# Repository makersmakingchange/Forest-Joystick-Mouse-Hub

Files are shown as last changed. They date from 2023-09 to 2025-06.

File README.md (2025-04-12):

# Forest Joystick Mouse Hub

## Overview
The Forest Hub enables a user to connect an analog joystick and up to four assistive switches to emulate a USB Mouse or USB Gamepad. As a USB Mouse, the joystick controls cursor movement and the assistive switches activate the left mouse button, right mouse button, middle mouse button, and scroll. As a USB Mouse, the joystick maps to the joystick/thumbstick and the assistive switches map to the joystick buttons. An additional assistive switch can be attached to the Hub to cycle between three setting slots and change the output mode between USB Mouse mode and USB Gamepad mode.

The device is comprised of a custom printed circuit board, off-the-shelf electronics, and 3D printed parts. The overall cost of materials for a single build is about $100. The individual unit cost cost is closer to $55. 

The Forest Hub is open assistive technology (OpenAT). Under the terms of the open source licenses, the device may be built, used, and improved upon by anyone.

Last updated: 2024-Apr-17
The latest version (V2.1) includes a new easier to use LED jig, updated firmware with center calibration, and updated documentation.
An updated version of the PCB and enclosure has been released (V2.0.1, 2024-Feb-20). The last version of the Forest Hub (v2.0.1) has been built and tested.

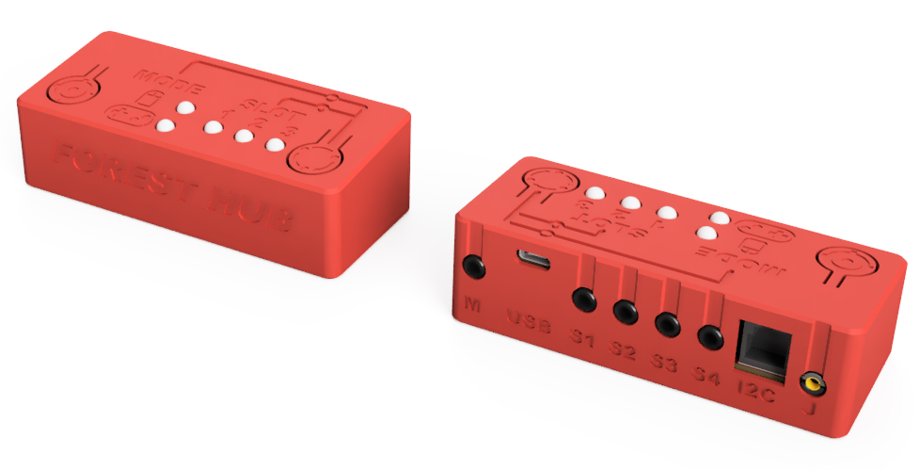
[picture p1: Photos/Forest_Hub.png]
A Forest Hub in a red enclosure.


MMC Assistive Device Library Listing: https://makersmakingchange.com/s/product/forest-joystick-mouse-hub/01tJR000000E4bdYAC

## OpenAT Joysticks
This design is part of the [OpenAT Joystick Project](https://github.com/makersmakingchange/OpenAT-Joysticks), a collection of open source designs for digital access and adapted gaming.  

## How to Obtain the Device
### 1. Do-it-Yourself (DIY) or Do-it-Together (DIT)

This is an open-source assistive technology, so anyone is free to build it. All of the files and instructions required to build the device are contained within this repository. Refer to the Maker Guide below.

### 2. Request a build of this device

If you would like to obtain a Forest Hub, you may submit a build request through the [MMC Assistive Device Library Listing](https://makersmakingchange.com/s/product/forest-joystick-mouse-hub/01tJR000000E4bdYAC) to have a volunteer maker build the device. As the requestor, you are responsible for reimbursing the maker for the cost of materials and any shipping.

### 3. Build this device for someone else

If you have the skills and equipment to build this device, and would like to donate your time to create the switch for someone who needs it, visit the [MMC Maker Wanted](https://makersmakingchange.com/maker-wanted/) section.

## Build Instructions

### 1. Read through the Maker Guide

The [Maker Guide](/Documentation/Forest_Hub_Maker_Guide.pdf) contains all the necessary information to build the device.

### 2. Use the Maker Checklist
Use the Maker Checklist in the [Maker Guide](/Documentation/Forest_Hub_Maker_Guide.pdf) to confirm details and customization options with the user.

### 3. Order the Custom Printed Circuit Board (PCB)
The manufacturing files for the PCB are located in the [PCB_Build_Files](/Build_Files/PCB_Build_Files/) folder.

### 4. Order the Off-The-Shelf Components

The [Bill of Materials](/Documentation/Forest_Hub_BOM.xlsx) lists all of the parts and 3D printed components required to build the device. 

### 5. Print the 3D Printable components

The print files can be found in the [/Build_Files/3D_Printing_Files](/Build_Files/3D_Printing/) folder.

### 6.  Assemble the Device

Reference the Assembly Guide section in the [Maker Guide](/Documentation/Forest_Hub_Maker_Guide.pdf) for the tools and steps required to build the device.

## Files
### Documentation
| Document             | Version | Link |
|----------------------|---------|------|
| Design Rationale     | 2.1     | [Forest_Hub_Design_Rationale](/Documentation/Forest_Hub_Design_Rationale.pdf)     |
| Maker Guide          | 2.1     | [Forest_Hub_Maker_Guide](/Documentation/Forest_Hub_Maker_Guide.pdf)     |
| Bill of Materials    | 2.1     | [Forest_Hub_Bill_of_Materials](/Documentation/Forest_Hub_BOM.csv)     |
| User Guide           | 2.1     | [Forest_Hub_User_Guide](/Documentation/Forest_Hub_User_Guide.pdf)    |
| Changelog            | 2.1     | [Changes](Changes.txt)     |

### Design Files
 - [CAD design Files](/Design_Files/CAD_Design_Files)
 - [PCB Design Files](/Design_Files/PCB_Design_Files)

### Build Files
 - [3D Printing Files](/Build_Files/3D_Printing_Files)
 - [PCB Build Files](/Build_Files/PCB_Build_Files/)
 - [Firmware Files](/Build_Files/Firmware_Files)

## License
Copyright (c) 2023 Neil Squire Society.

This repository describes Open Hardware:
 - Everything needed or used to design, make, test, or prepare the Forest Hub is licensed under the [CERN 2.0 Weakly Reciprocal license (CERN-OHL-W v2) or later](https://cern.ch/cern-ohl ) .
 - All software is under the [GNU General Public License v3.0 (GPL-3.0)](https://www.gnu.org/licenses/gpl.html).
 - Accompanying material such as instruction manuals, videos, and other copyrightable works that are useful but not necessary to design, make, test, or prepare the Forest Hub are published under a [Creative Commons Attribution-ShareAlike 4.0 license (CC BY-SA 4.0)](https://creativecommons.org/licenses/by-sa/4.0/) .

You may redistribute and modify this documentation and make products using it under the terms of the [CERN-OHL-W v2](https://cern.ch/cern-ohl).
This documentation is distributed WITHOUT ANY EXPRESS OR IMPLIED WARRANTY, INCLUDING OF MERCHANTABILITY, SATISFACTORY QUALITY AND FITNESS FOR A PARTICULAR PURPOSE.
Please see the CERN-OHL-W v2 for applicable conditions.

Source Location: https://github.com/makersmakingchange/Forest-Joystick-Mouse-Hub

List of open source licenses. Hardware: CERN-OHL-W-2.0, Software: GPL-3.0-or-later, Documentation: CC-BY-SA-4.0.

## Attribution

The [Adafruit QT Py](http://www.adafruit.com/products/4600) development board was designed by Limor Fried/Ladyada from Adafruit. The PCB design is [available open source](https://github.com/adafruit/Adafruit-QT-Py-PCB) under a CC-BY-SA license.

The concept for the Forest Hub was based on the [Enabled Controller Mini](https://github.com/milador/Enabled-Controller-Mini) by [Milador](https://github.com/milador).

### Contributors
- Jake McIvor, Neil Squire Society. Concept generation, enclosure design, schematic and PCB design, coding, documentation, testing.
- Milad Ha, Neil Squire Society. Schematic and PCB design, coding.
- Josie Versloot, Neil Squire Society. Concept generation, coding, documentation.
- Derrick Andrews, Neil Squire Society. Schematic design.
- Stephen Moyer, Neil Squire Society. Concept generation.
- Tyler Fentie, Neil Squire Society. Concept generation

## Open Source Hardware Certification

The Forest Hub has been certified as open source hardware by the Open Source Hardware Association under the OSHWA UID [CA000033](https://certification.oshwa.org/ca000033.html).

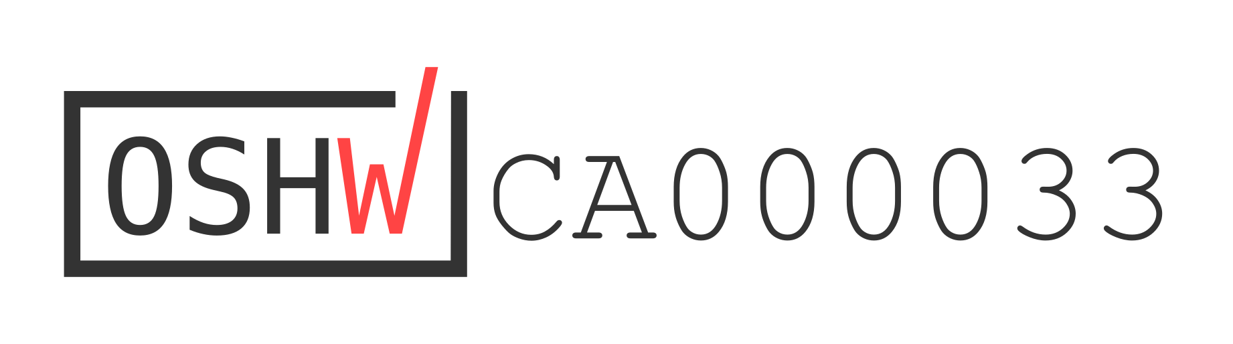
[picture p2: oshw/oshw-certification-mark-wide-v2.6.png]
Open Source Hardware Certification Mark for Forest Hub: CA000033


---
<!-- ABOUT MMC START -->
## About Makers Making Change
[Makers Making Change Logo](https://www.makersmakingchange.com/)

Makers Making Change is a program of [Neil Squire](https://www.neilsquire.ca/), a Canadian non-profit that uses technology, knowledge, and passion to empower people with disabilities.

Makers Making Change leverages the capacity of community based Makers, Disability Professionals and Volunteers to develop and deliver affordable Open Source Assistive Technologies.

 - Website: [www.MakersMakingChange.com](https://www.makersmakingchange.com/)
 - GitHub: [makersmakingchange](https://github.com/makersmakingchange)
 - Bluesky: [@makersmakingchange.bsky.social](https://bsky.app/profile/makersmakingchange.bsky.social)
 - Instagram: [@makersmakingchange](https://www.instagram.com/makersmakingchange)
 - Facebook: [makersmakechange](https://www.facebook.com/makersmakechange)
 - LinkedIn: [Neil Squire Society](https://www.linkedin.com/company/neil-squire-society/)
 - Thingiverse: [makersmakingchange](https://www.thingiverse.com/makersmakingchange/about)
 - Printables: [MakersMakingChange](https://www.printables.com/@MakersMakingChange)

### Contact Us
For technical questions, to get involved, or to share your experience we encourage you to [visit our website](https://www.makersmakingchange.com/) or [contact us](https://www.makersmakingchange.com/s/contact).
<!-- ABOUT MMC END -->

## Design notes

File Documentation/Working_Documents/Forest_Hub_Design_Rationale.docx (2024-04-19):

# Introduction

The Forest Hub is an open-source interface that connects to an analog joystick and one or more assistive switches and emulates an HID Mouse and/or HID Gamepad. The device is intended for people who are unable to use traditional input devices like a computer mouse or gaming controller.

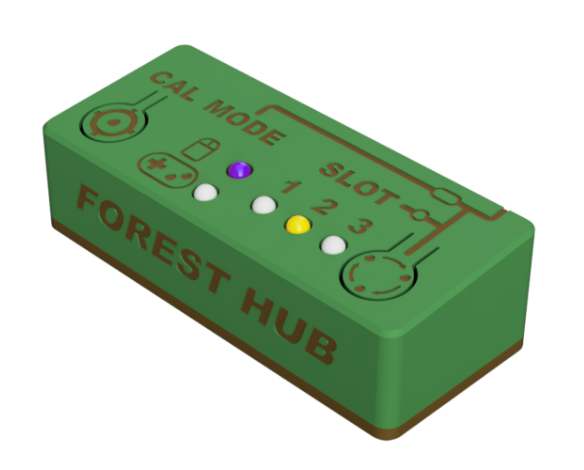
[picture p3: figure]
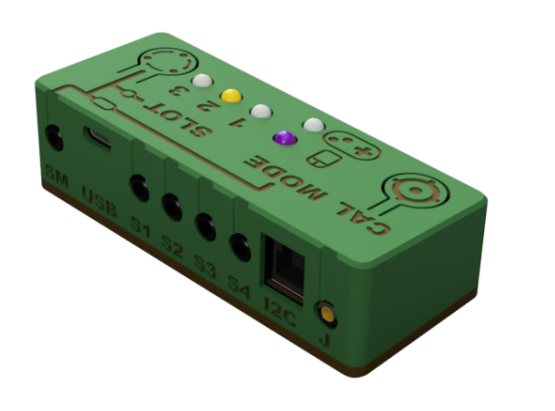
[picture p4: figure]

# Research

## Existing Commercial Options

Title | Quester-switchbox
Link | https://www.pretorianuk.com/quester-switchbox
Author
License
Cost
Notes

## DIY Designs

Title | Enabled Controller Mini
Link | https://github.com/milador/Enabled-Controller-Mini
Author | Milad Hajihassan
License | CC-BY-NC-SA
Cost
Notes

Title | Enabled Controller
Link | https://github.com/milador/Enabled-Controller
Author | Milad Hajihassan
License | CC-BY-NC-SA
Cost
Notes

Title | Enabled Controller Wireless
Link | https://github.com/milador/Enabled-Controller-Wireless
Author | Milad Hajihassan
License | CC-BY-NC-SA
Cost
Notes

# Requirements

## Goals

G01 | Cost-effective
G02 | Maker Manufacturable
G03

## Functional Requirements

F01 | Able to operate as both a USB Mouse and a USB Joystick
F02 | User should have ability to adjust cursor speed.
F03 | User should have ability to initiate calibration.

## Non-functional Requirement

NF01
NF02
NF03

## Constraints

C01 | 10 x 10 cm Maximum PCB Size for cost-effective manufacturing
C02 | 8 x 10 cm Maximum PCB size for free version of Eagle

# Ideation

## Key Features

Number of Ports – how many inputs are available for assistive switches

- 4 + 1 for mode/slot switching

Device Buttons – what controls are available on the device itself?

- Mode Switch
- Calibration

Mouse function

- Core Functions
  - Left click
  - Right click
  - Scroll
  - Middle click
- Additional functions
  - Double click

User feedback – what indicators are required for the user to determine the state and/or settings of the device?

- Power (is the device powered / on)
- Output Mode (is the device outputting Mouse or Gamepad)
- Slot / Level / Profile (different

Bluetooth Indicator?

User feedback methods – how are the indicators conveyed?

- Individual lights / LEDs
- LED colour
- Display / LCD
- Sound

Slots – enable the user to change between different settings / mappins

- Two Output Indicators and Three Slot Indicators
- Output Indicators
  - Mouse
  - Gamepad
- Three Slot Indicators
  - Slot 1
  - Slot 2
  - Slot 3

Calibration – how is a joystick calibrated when attached? When swapped?

- Neutral position calibration
- Extents calibration

## Customizability

How can the device be customized to tailor it to the user?

- Enclosure color
- Control the color of the neopixels
- Control the color and pattern of the microcontroller neopixel
  - Graphic
  - Custom lithophane

## User Experience

Adjust Mouse

- Adjust cursor speed

Switch Slots

- Short press to switch slots
- Long press to switch between mouse and joystick
- LEDs Indicating slot and output mode

### Calibration

Short press Calibration button to start neutral position reset.

Long press calibration button to start extent calibration

Set Neutral position on startup

## Layout

- USB in same direction as the inputs
- USB in other direction as the inputs

Mode switch / button / lights in proximity

# Conceptual Design

## Concept A: Microcontroller + Custom PCB

This concept is based on a microcontroller and a custom PCB that would house the various switch jacks and user interface elements like LEDs and buttons.

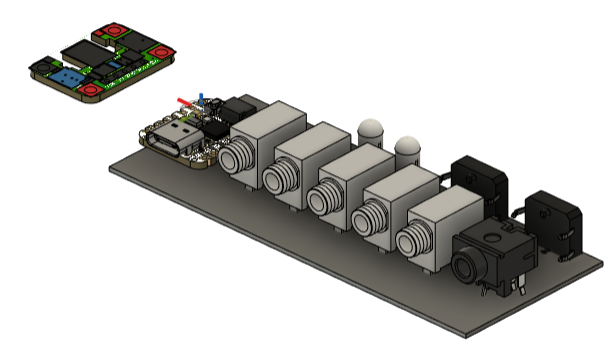
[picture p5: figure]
CAD screenshot of a layout concept with USB and switch jacks facing front

4+1 Inputs, 5 Neopixels, Buzzer, SAMD21

- Qt Py SAMD21
- (2) Analog Joystick Jack
- (4) Switch Jacks A, B, C, D
- (1) Mode Button, Calibration button and Mode Switch Jack
- (1) Output Neopixels
  - Mouse Output Neopixel LED
  - Joystick Output LED
  - Slot 1 Neopixel LED
  - Slot 2 Neopixel LED
  - Slot 3 Neopixel LED
- (1) Buzzer
- (2) External i2C connection

### User Interface – Neopixels

5mm Through hole NeoPixels could be utilized to provide custom spacing and arrangement of the indicator lights. These can be driven using a single pin, have adjustable brightness, and could be used in different colours based on user preference.

NeoPixel Diffused 5mm Through-Hole LED – 5 Pack

- Adafruit (https://www.adafruit.com/product/1938), $4.95 USD
- Mouser (https://www.mouser.ca/ProductDetail/Adafruit/1938?qs=GURawfaeGuAkVClyRWI8wg%3D%3D), $7.18 CAD

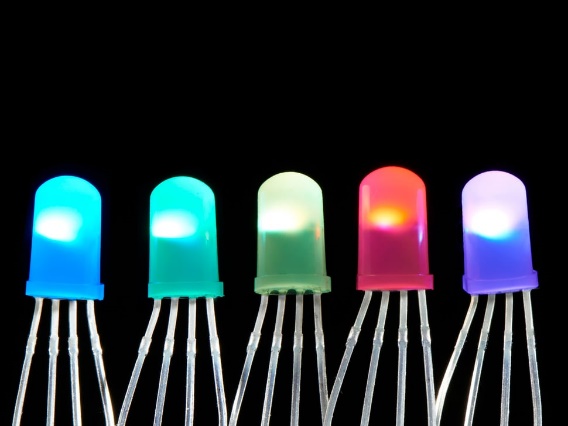
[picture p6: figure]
Five NeoPixel Diffused 5mm Through-Hole LEDs glowing rainbow

Figure 1. Adafruit NeoPixel Diffused 5mm Through-Hole LED - 5 Pack

## Concept B: GPIO Expander or Seesaw-based PCB

This concept is based around a microcontroller that is connected via I2C to a GPIO Expander mounted on a custom PCB. The custom PCB is intended to be a more general purpose I2C device where multiple switch inputs, buttons, and indicator lights could be controlled by a variety of microcontrollers.

## Concept C: Feather dev Board + Feather Wings

This concept would utilize the Feather ecosystem for the development board and a combination of Feather Wings and i2C dev boards for additional functions.

OLED Display FeatherWing: https://www.adafruit.com/product/4650 128x64 128x64 (https://www.adafruit.com/product/4650%20128x64%20128x64) OLED Display + 3 integrated buttons.

As a bonus, the Adafruit Joy FeatherWing, which has a built in thumbstick and buttons could be connected to provide an all-in-one solution.

Adafruit Joy FeatherWing for all Feathers

- Adafruit (https://www.adafruit.com/product/3632), $9.95 USD

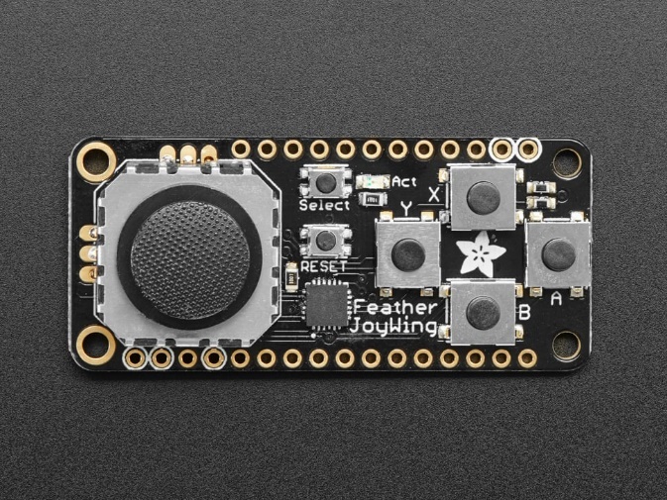
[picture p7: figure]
Close up of a Adafruit Joy FeatherWing for all Feathers.

Figure 2. Adafruit Joy FeatherWing. https://www.adafruit.com/product/3632

## Concept D: DIY / 3D Printed PCB

This concept would avoid the use and associated cost of a custom PCB.

### Switch Jacks

Switch and joystick ports could be done using panel mount connectors and individually soldered wires, or using a combination of breadboard-friendly switch jacks soldered into proto board and TRRS breakout boards.

Adafruit TRRS Jack Breakout Board

- Adafruit (https://www.adafruit.com/product/5764), $1.75 USD
- Mouser (https://www.mouser.ca/ProductDetail/Adafruit/5764?qs=VJzv269c%252BPajUYy87VZJFw%3D%3D), $2.54 CAD

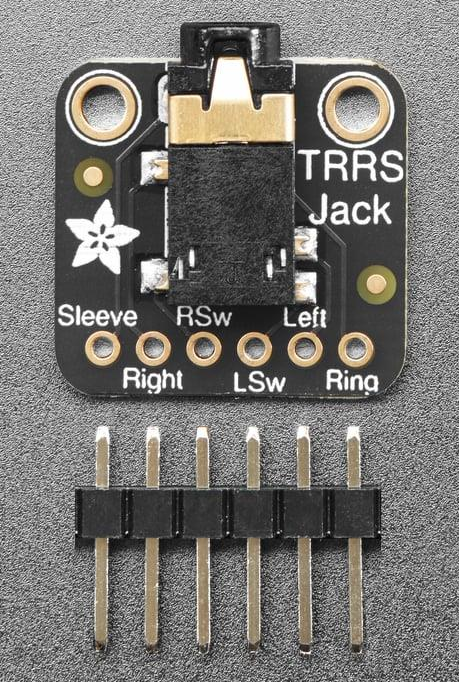
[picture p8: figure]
Adafruit TRRS Breakout Board

Figure 3. Adafruit TRRS Jack Breakout Board.

Adafruit Breadboard Friendly 3.5mm Stereo Headphone Jack

- Adafruit (https://www.adafruit.com/product/1699), $0.95 USD
- Mouser (https://www.mouser.ca/ProductDetail/Adafruit/1699?qs=GURawfaeGuChLGW1wGYm8w%3D%3D), $1.38 CAD

### External I2C Connection

Sparkfun RJ11 / Rj25 Breakout

- Mouser (https://www.mouser.ca/ProductDetail/SparkFun/BOB-14021?qs=FNcb6ahWXRxYfdHxmKm33A%3D%3D), $2.83

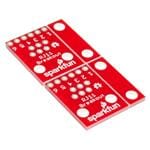
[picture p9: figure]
SparkFun BOB-14021 Enlarged Image

Figure 4. Sparkfun RJ11 Breakout

## Accessories

There are a couple options for I2C joysticks that could be used in place of the Analog Joystick:

Adafruit Mini I2C Gamepad with seesaw – STEMMA QT / QWiic

- Adafruit (https://www.adafruit.com/product/5743), $7.50 USD
- Mouser (https://www.mouser.ca/ProductDetail/Adafruit/5743?qs=VJzv269c%252BPaAyxDqKbcNxg%3D%3D), $10.88 CAD; No stock in Mouser (0 as of 2023-Sep-08)
- DigiKey (https://www.digikey.ca/en/products/detail/adafruit-industries-llc/5743/20370632.), $10.79 CAD; Low stock in Digikey (4 as of 2023-Sep-08)

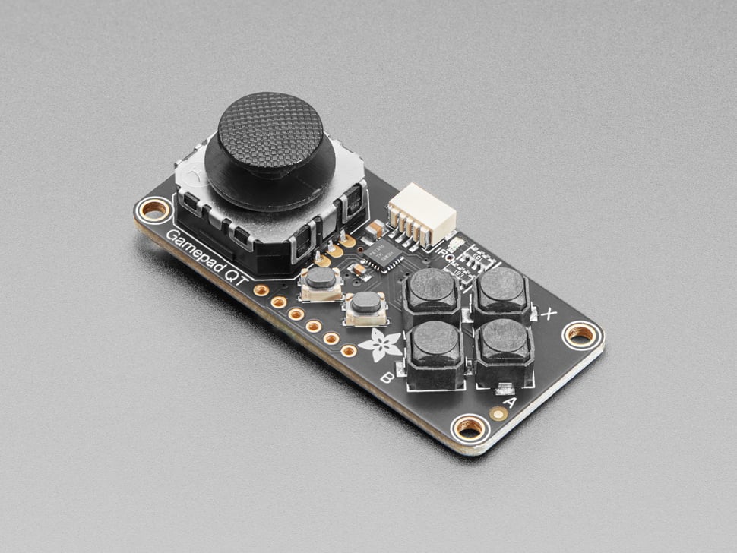
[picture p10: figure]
Angled shot of small rectangular gamepad PCB with thumbstick.

Figure 5. Adafruit Mini I2C Gamepad with seesaw - STEMMA QT / Qwiic

## Concept Selection

Concept A was selected as a custom PCB made the most sense for simple, reliable maker manufacturing in the larger quantities expected as part of the ATP Grant. A custom-PCB free version should also be designed to help manage the cost and mitigate the barriers of ordering PCBs for single builds.

# Detailed Design

## Naming

Tree theme:

- Canopy
- Root
- Hub
- Trunk – where the branches connect
- Stem
- Branch
  - Branch Joystick Mouse Hub?
  - The Branch – Joystick Mouse Hub
  - The Branch Hub
  - The Branch Joystick Hub
  - The Branch Joystick Hub – for Gamepad and Mouse Application
- Dendro (relating to trees)
- Arbor (
  - Arboreal
  - Arbor Hub
  - ArborLink
  - Arborium
- Forest
  - Sylvan
    - Silva – latin for forest or wood
  - Silvihub
  - Silvadaptor
  - Boreal
  - Taiga
  - Acadian

Branch

- Bough

Earth / Soil / Dirt / Loam

- Terra
- Topsoil

Canopy

- Crown
- foliage

Word origins

- Dendro- greek dendron – tree
- Xylo- Greek “Xulon” – wood
- Silva- latin silva – “forest” or “woodlands”
- Lignum- latn lignum “wood”
- Arbor- latin arbor – “tree”
- Sylva – variant of silva – forest or wooded area
- Phyto – Greek phyton – “plant”
- Myco- Greek mukes – “fungus” / “mushroom”
- ~~P~~~~e~~~~d~~~~-~~ ~~Greek~~ ~~pedon~~ ~~– “Soil” or “ground”~~

Connector / Adapter / Interface

- Link
- Connect
- Nexus
- Port
- Node
- Plug
- Adaptor
- Hub
- ~~Dongle~~
- ____ Joystick Interface
- ____ Joystick Mouse Interface
- ____ JoyMouse Interface

Mycorrhizal – My-co-rye-zal

| Mycohub | Root
Branch Joystick Mouse Hub | | Dendrohub
| Branch Hub | Root Hub
| ArborHub | ~~Denrodongle~~
| | ~~TerraHub~~
Arbor Interface
Arbor Joystick Interface | (AJI?)
___JoyMouse Interface
Canopy
Forest
Branch
Boreal
Canopy Connect Joystick Mouse Interface
Canopy Connect Joystick Mouse Hub

### Short List

Arbor Joystick Mouse Hub | “Arbor Hub”
Boreal Joystick Mouse Hub | “Boreal Hub”
Branch Joystick Mouse Hub | “Branch Hub”
Canopy Joystick Mouse Hub | “Canopy Hub”
Forest Joystick Mouse Hub | “Forest Hub”

Final Selection: Forest Joystick Mouse Hub

## Enclosure Design

### UI Layout

The Enabled Controller Mini has connections on all sides of the enclosure, and we received feedback that this was undesirable and made it more difficult to manage cables. The decision was to have the reduce the number of cable surfaces to 1 or 2. Two main options were considered: inputs on one side and output on the other side, and everything on one side. The decision was to move all cable connections to the back of the enclosure to make it easier to manage cables, and minimize the visual clutter for the user.

Several options were also considered for the placement of the main user indicators and controls. Locating both the buttons and the indicators on the top surface was selected. This made it easier to activate the buttons with a single hand by pressing down on the enclosure (and avoiding pressing on the side which could cause the enclosure to slide). It also made it possible to put the indicators and controls in proximity to associate their function, and provided greater flexibility in LED positioning.

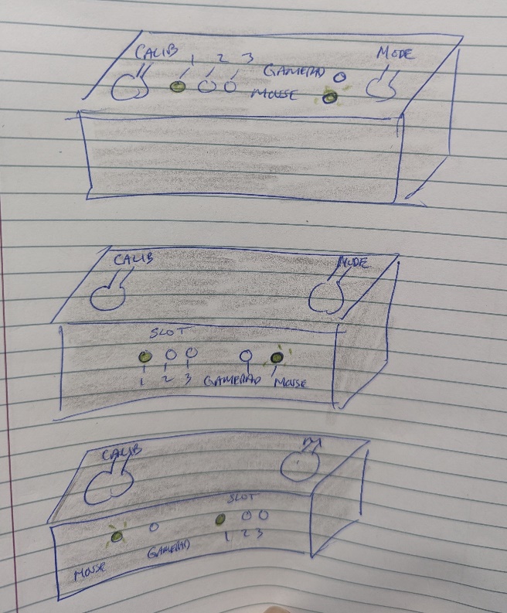
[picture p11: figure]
Sketch of three layout concepts: lights and buttons on top; buttons on top and lights on side; and buttons on top and lights swapped left to right.

Figure 6. Indicator Layout Options

### Graphics / Labelling

#### Switch Inputs Jack Naming

S1, S2, S3, and S4 were used for the input switches to help reduce confusion between ABCD (e.g., A and B from a gaming controller) or 1234.

#### Mode Button

The mode button consists of three circles connected by arrows.

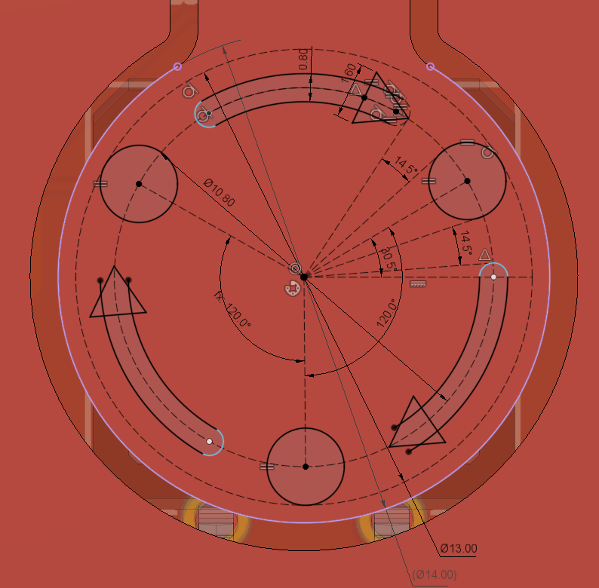
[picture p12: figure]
CAD screenshot of mode button label

Figure 7. Mode Button Graphic.

#### Calibration Button

A bullseye design was chosen for the calibration button.

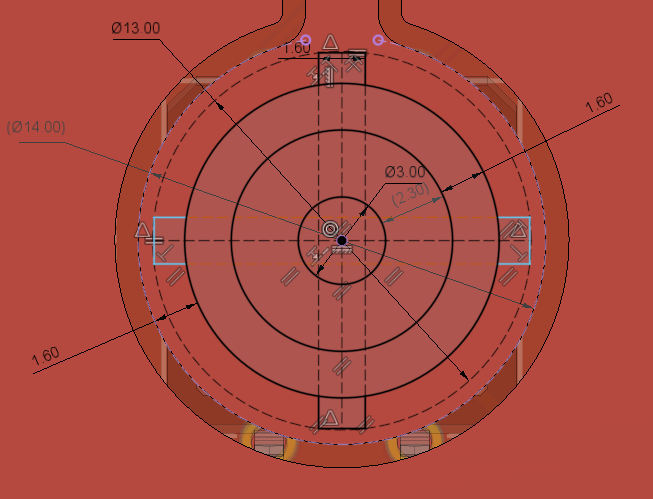
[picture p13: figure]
CAD screenshot of calibration button label.

Figure 8. Calibration Button Graphic.

#### Mouse Output LED

A top-down graphic of a computer mouse was selected. A mouse cursor, mouse animal, and the word “mouse” were also considered. The top-down graphic was the most appropriate given the function and the space available.

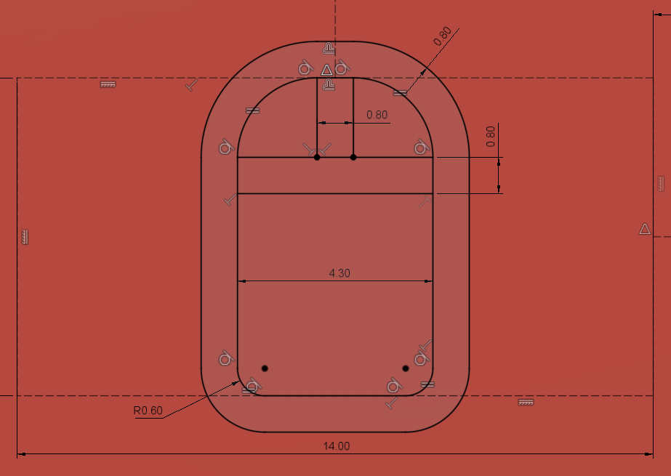
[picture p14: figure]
CAD screenshot of mouse indicator label

Figure 9. Mouse Output LED Graphic.

#### Joystick Output LED

A top-down graphic of a traditional gamepad with a directional pad and two buttons was selected.

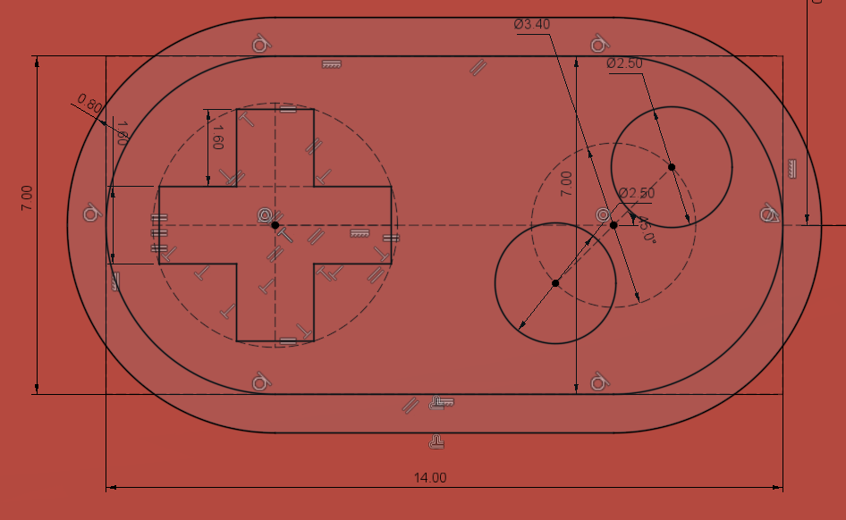
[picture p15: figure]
CAD screenshot of gamepad output indicator label

Figure 10. Joystick Output LED Graphic.

## Electronics

Electronics Requirements

1. 5X mono jack inputs
2. 1X analog joystick input
3. 1X Buzzer
4. 2X Tactile Switches – Mode Switch and Calibration
5. 1X RJ11 External i2C Connection
6. 5X NeoPixels

### Schematic

#### Buzzer

A buzzer was added to provide audible feedback for those that are unable to see the feedback lights on the enclosure. A PS1240 Piezo Buzzer from Adafruit (https://www.adafruit.com/product/160) was selected as it was used on a similar project to provide audible feedback (the ASTA Switch Training Aid).

To minimize components, a simple circuit with a resistor was selected. A 100 ohm resistor was chosen.

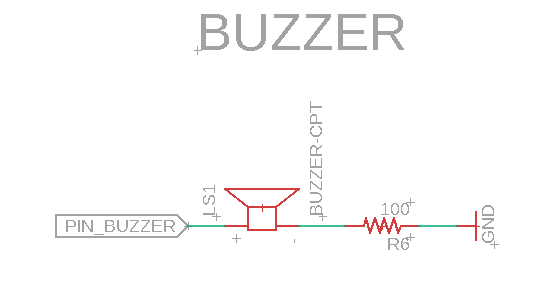
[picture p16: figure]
Buzzer schematic.

Figure 11. Simple Buzzer Circuit

To maximize sound output, a slightly more complicated circuit with another resistor and a drive transistor would be required. Initial testing showed that the volume and response is likely sufficient.

#### Multiple Button Input Resistor Ladder

There are more pins required than available GPIO on the microcontroller. To maintain function and the microcontroller, a method for reading multiple input via a single GPIO line was required.

A few options were considered, and ultimately the following circuit was selected so that each input and combination of multiple inputs could be detected by the analog input line. The Mode Switch Jack (SW_M) was chosen as the final leg on the ladder so that any cable or switch resistance would have a smaller effect.

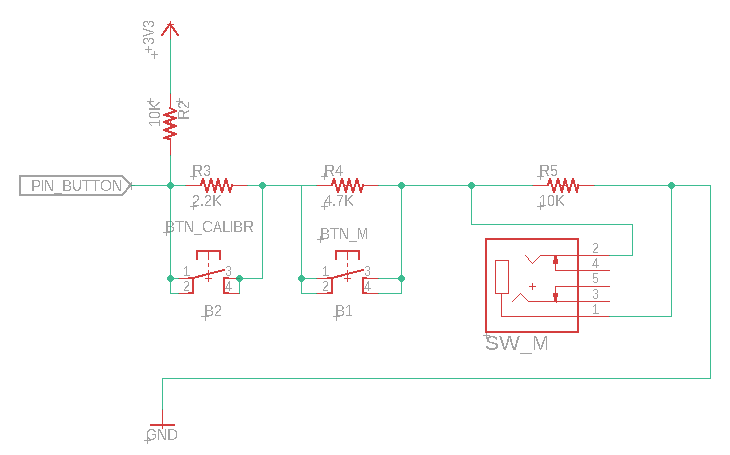
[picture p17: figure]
Schematic for reading two buttons and one switch using single analog input

Figure 12. Analog Multiple Input Schematic

Table 1. Resistor Ladder Values

Resistor | Item | Value
R2 | Voltage Divider | 10K
R3 | B2 / Calibration Button | 2.2K
R4 | B1 / Mode Button | 4.7K
R5 | SW_M / Mode Switch Jack | 10K

Table 2. Theoretical Analog Voltages

B2 State | B1 State | SW_M State | Resistance Top | Resistance Bottom | Voltage | Steps
1 | 1 | 1 | 10000 | 16900 | 2.1 | 643
1 | 1 | 0 | 10000 | 14700 | 2.0 | 609
1 | 0 | 1 | 10000 | 12200 | 1.8 | 563
1 | 0 | 0 | 10000 | 10000 | 1.7 | 512
0 | 1 | 1 | 10000 | 6900 | 1.3 | 418
0 | 1 | 0 | 10000 | 4700 | 1.1 | 327
0 | 0 | 1 | 10000 | 2200 | 0.6 | 185
0 | 0 | 0 | 10000 | 0 | 0.0 | 0

### Pin allocation

The following table lists the inputs and outputs

Table 3: Pin Allocation

Item | Voltage | Gnd | Digital | Analog | Assignment
Joystick Jack | 1 | 1 | | 2 | A0, A1
Switch S1 Jack | | | 1 | | A2
Switch S2 Jack | | | 1 | | A3
Switch S3 Jack | | | 1 | | TX
Switch S4 Jack | | | 1 | | MO
Switch M Jack | | | 1 | | MI (Resistor Network)
Mode Button | | | | 1 | MI (Resistor Network)
Calibration Button | | | | (shared with Mode) | MI (Resistor Network)
Buzzer | | | 1 - PWM | | SCK
Neopixels | 1 | 1 | 1

### I2C Connection: RJ11Connector

A phone cable and a RJ11 Connector approach was selected for the external I2C connection as it has been used in another Open Source assistive technology device, the FABI. There is a system that uses an RJ45 and ethernet cable to conduct I2C over distances (e.g., SparkFun QwiicBus

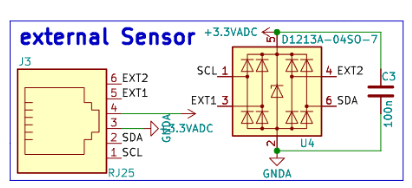
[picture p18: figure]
Schematic for FABI external sensor RJ25

Figure 13. FABI External Sensor Wiring Scheme. https://github.com/asterics/FABI/blob/SRC_v3.0/hardware/FABI_schematic.pdf

Table 4. I2C - RJ11 Wiring Options

Pin | Option A - FABI Connection | Option B – Match Sparkfun Adapter | Option C – Match i2C Module Breakout Board
1 | SCL | GND | GND
2 | SDA | GND | 3.3V
3 | GND | 3.3V | GND
4 | 3.3V | SDA | SCL
5 | Not connected | SCL | SDA
6 | Not connected | GND | GND

Three options were considered for how to wire connect the I2C connections to the RJ11 connector.

- Option A would be to match FABI External Sensor Wiring Scheme. This would have been the preferred option, but it is common for cables and connectors to only have the inner 4 pins connected (i.e., 2,3,4,5).
- Option B would make it possible to solder an RJ11 breakout directly to the Sparkfun STEMMA QT / Qwiic Adapter
- Option C would make it possible to solder an RJ11 breakout directly to a STEMMA QT breakout board.

Version 1.0 of the PCB was released with Option C. It was later discovered that this doesn’t work as intended, so later versions of the PCB (V2.0 and up) use Option B. This was also chosen to be consistent with the LipSync (https://github.com/makersmakingchange/LipSync) design.

## Neopixel Soldering Jig

The five Neopixel LEDs are spaced higher than the PCB so they partially protrude through the top enclosure. To reliably set this height, a 3D printed jig is used. The bottom of the LEDs are at 3 different heights from the board: 11.5, 12.0, and 12.5 mm from the board.

The initial jig design was a single 3D printed piece. The spacing between the 4 leads was too small to have separate holes for each, so a single cavity was used for each.

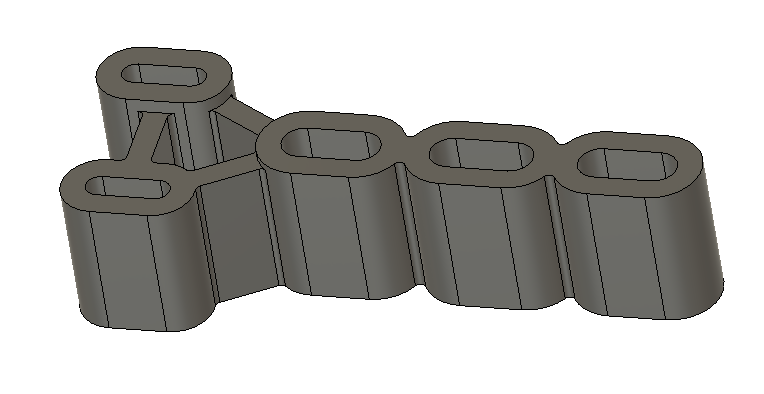
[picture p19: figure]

Figure 14. LED Soldering Jig (V1.0)

Assembly with this jig was extremely difficult, as the leads for each of the 5 jigs (i.e., 20 total) had to be aligned into the corresponding holes in the PCB without being able to see them. Several alternatives were considered, including splitting the jig in to two parts, or five individual parts. The option that was chosen for the next version features a similar design to the original with one-piece that has windows to make it easier to see and insert the individual leads.

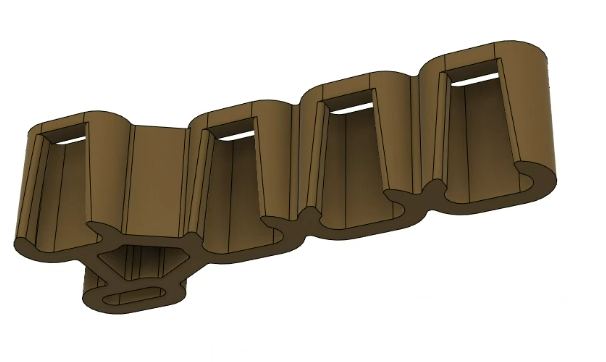
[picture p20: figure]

Figure 15. LED Soldering Jig (V2.0)

# Firmware

## Parsing Multiple Switches on Analog Pin

The theoretical values for each of the combination of switch closures is presented in Table 5. This is calculated based on the nominal resistor values. To resolve which combination is pressed, thresholds are setup at midway between the different steps. This should accommodate for any variation in true resistor values due to their tolerance. When the measured voltage is below the threshold, that combination of buttons/switches is likely pressed.

Table 5. Theoretical Voltage for Switch Combinations

SW_M | B1 | B2 | Theoretical Steps | Threshold
Off | Off | Off | 643
Off | Off | On | 609 | 626
Off | On | Off | 562 | 586
Off | On | On | 512 | 538
On | Off | Off | 418 | 465
On | Off | On | 327 | 373
On | On | Off | 184 | 256
On | On | On | 0 | 93

## Non-Volatile Storage

The Forest Hub needs non-volatile storage to store settings when the device is powered off.

The Adafruit QT Py does not have any EEPROM, but is able to use flash. The FlashStorage library (https://github.com/cmaglie/FlashStorage) is used to handle it more easily.

Variable | Variable Type | Note
isConfiguredFlash | bool | False when first flashed, True after first run
deviceNumberFlash | int
modelNumberFlash | int
versionNumberFlash | int | Number to track firmware version
deadzoneLevelFlash | int
cursorSpeedLevelFlash | int
operatingModeFlash | int | Operating Mode (0
ledBrightnessFlash | int | 0-255 LED Brightness
slotNumberFlash | int | Track index of current settings slot
xOutputMinimumFlash | int | Calibration
xOutputMaximumFlash | int | Calibration
yOutputMinimumFlash | int | Calibration
yOutputMaximumFlash | int | Calibration
xNeutralFlash | int | Calibration
yNeutralFlash | int | Calibration
ledColorRFlash | int | User LED color - red
ledColorGFlash | int | User LED color - green
ledColorBFlash | int | User LED color - blue

## Calibration

Calibration is used to ensure that the joystick outputs zeros when the input joystick is released to mechanical neutral, and that the output is maxed then the input joystick is moved to the maximum extent.

### Center Reset

The center reset measures the neutral position of the joystick: xNeutral and yNeutral. These numbers are subtracted from the main reading so that when the joystick is in the neutral position, the output is zeroed (i.e., x=0, y=0). The calibration is saved to and read from flash memory, (e.g., xNeutralFlash, yNeutralFlash), though this doesn’t do much as the calibration is triggered every time the device is powered.

### Extents

The extents calibration ensures that the output is maximized when the joystick is moved to its most extreme position. Currently, these values are just set to a default constant value (e.g., +/- 127) – there is no method or way to dynamically measure the physical min and max of each joystick axis.

These values are set and retrieved from memory: xOutputMinimumFlash, xOutputMaximumFlash, yOutputMinimumFlash, yOutputMaximumFlash.

# Version 0.1 – PCB Prototype

## V0.1 Features

The initial prototype of the Forest Hub included the following features:

1. (1) Adafruit QT Py SAMD21 Development Board
2. (1) Analog Joystick Input via 3.5 audio TRRS jack
3. (4) Assistive Switch Inputs via 3.5 mm audio mono jacks
4. (1) Assistive Switch Input via 3.5 mm audio mono jack for mode/slot switching
5. (1) Built-in button for mode/slot switching
6. (1) Built-in button for calibration
7. (5) Multicolor LED lights for indicating current slot and output mode
8. (1) Accessory Connection via i2C connected to a RJ25 jack
9. (1) Piezo Buzzer for audio feedback

## V0.1 PCB

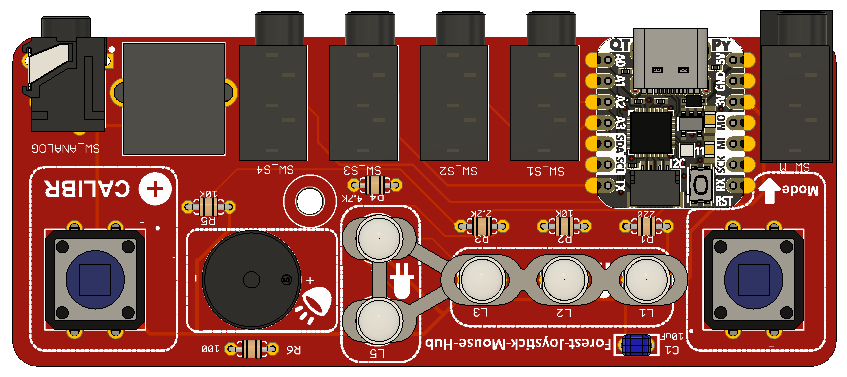
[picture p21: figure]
Top-down screenshot of initial PCB
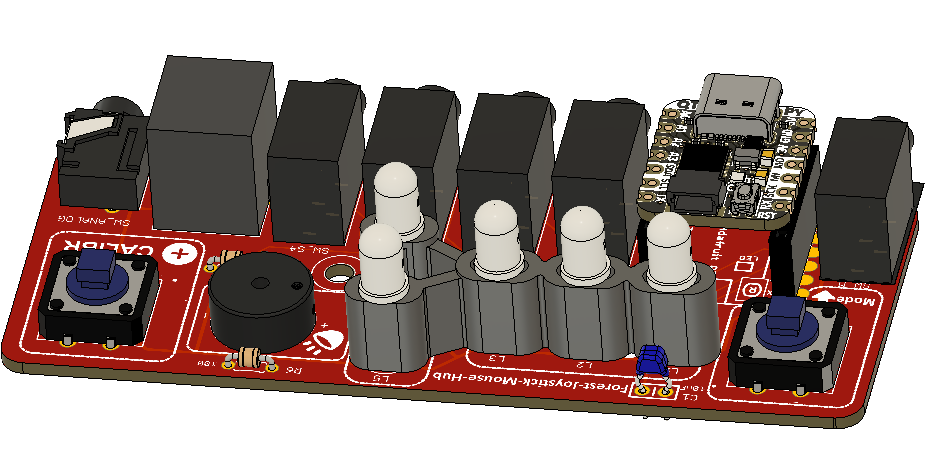
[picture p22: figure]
Isometric screenshot of initial PCB

## V0.1 Enclosure

The enclosure comprises a top and a bottom that are secured with a snap fit. A third 3D printed component acts as a jig to bring the LEDs up to the proper height to stick through the enclosure.

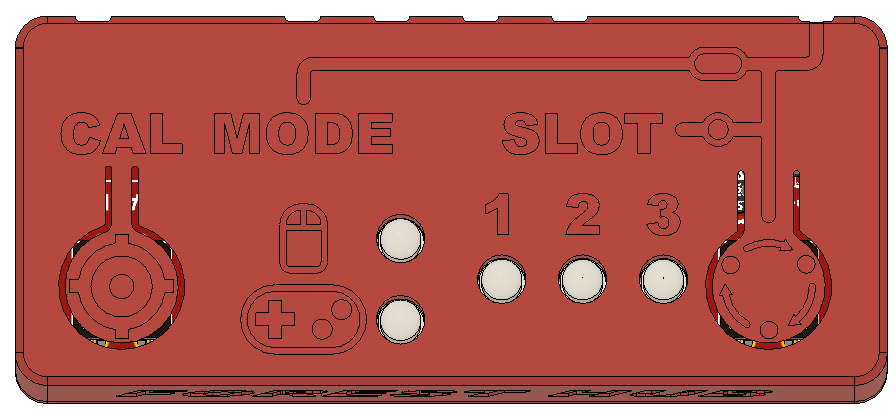
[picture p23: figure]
CAD screenshot of initial enclosure top
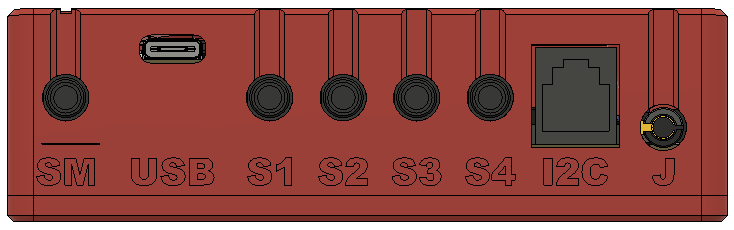
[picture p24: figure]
Cad Screenshot of initial enclosure rear
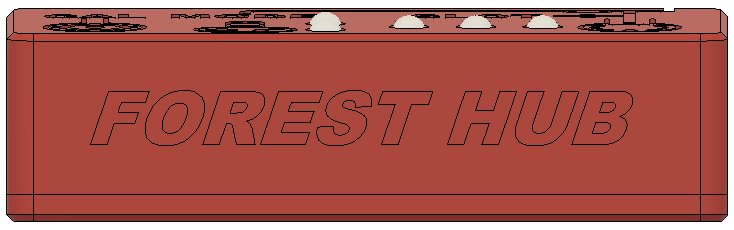
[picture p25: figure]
CAD screenshot of enclosure front showing Forest Hub label

## V0.1 Build Feedback

1. Some portions of the top enclosure didn’t print well – will require a near-perfect first layer to resolve some of the fine details.
2. The capacitor was added late and was not part of the prototype components order.
3. The resistors didn’t match the footprint – they were too long to fit properly and had to be soldered in awkwardly.
4. The RJ25 connector is positioned recessed a bit from the edge of the PCB and doesn’t match the other audio connectors. Because it is recessed into the enclosure, it is a little difficult to remove the plug when it is inserted.
5. The RJ25 connector has a different footprint than the Sparkfun RJ11 breakout board and is not compatible.
6. It was quite difficult to insert the Neopixel LEDs through the one-piece led soldering jig and into the holes in the PCB.
7. Soldering the Neopixels requires fine dexterity and skill to avoid bridging the connections.
8. The #4 screw didn’t thread properly into the base. (Note: This was a modelling error; the sketch was fixed, but the feature kept the original diameter).

## V0.1 Testing

1. The enclosure snap-fits do not securely retain the bottom to the top. If the enclosure is dropped (without the PCB), the parts fly apart.
2. The enclosure buttons need to be pushed further than expected to activate the internal buttons. (Note: There is a mismatch between the height of the ECAD model of tactile button and the actual component, resulting in a greater distance between enclosure button pusher and tactile button.)
3. All components are wired correctly and function – Neopixels, buttons, switch inputs, joystick input, buzzer, and I2C.

## V0.1 Opportunities for Improvement

1. PCB Changes
  a. ~~Add~~ ~~Open Source~~ ~~Hardware certification and logo to PCB~~
  b. Adjust positioning of RJ25 jack so that edge lines up with audio jacks
  c. Replace RJ25 component with one that has a compatible footprint with Sparkfun breakout board
  d. Ensure resistor footprint matches BOM model
  e. Add silkscreen label to RJ25 connector / I2C on board
2. Consider easier-to-solder LED options rather than Neopixel Leds
3. Add more robust enclosure snap-fit
4. ~~Fix enclosure PCB screw post so that it works with #4~~ ~~fastener~~
5. Add additional mounting hole or mounting features to support PCB
6. Investigate options for preventing reset when joystick cable is inserted / removed
  a. Switched jack?
7. Implements extents calibration

# Version 1.0

## V1.0 Features

The initial release of the Forest Hub includes the following features:

1. (1) Adafruit QT Py SAMD21 Development Board
2. (1) Analog Joystick Input via 3.5 audio TRRS jack
3. (4) Assistive Switch Inputs via 3.5 mm audio mono jacks
4. (1) Assistive Switch Input via 3.5 mm audio mono jack for mode/slot switching
5. (1) Built-in button for mode/slot switching
6. (1) Built-in button for calibration
7. (5) Multicolor LED lights for indicating current slot and output mode
8. (1) Accessory Connection via i2C connected to a RJ25 jack
9. (1) Piezo Buzzer for audio feedback

## V1.0 Opportunities for Improvement / Future Work

1. Consider easier-to-solder LED options rather than Neopixel Leds
2. Add additional mounting hole or mounting features to support PCB
3. Consider additional circuitry (i.e., driving transistor) for piezo buzzer to increase volume.
4. Investigate options for preventing reset when joystick cable is inserted / removed
  a. Switched jack?
5. Implements extents calibration
6. Develop non-custom PCB option
7. Provide access to microcontroller reset to make it easier to flash firmware

# Version 2.0 – Refined PCB

## V2.0 Changes

PCB Changes

1. Replaced RJ11 connector with same component that matches SparkFun RJ11 Breakout board.
2. Increased size of resistor footprint to match part
3. Increased size of capacitor footprint
4. Aligned RJ11 Jack with switch jacks
5. Flipped labels to orient board in natural usage orientation
6. Added additional silkscreen labels for component values

Firmware

1. Properly implemented neutral calibration.
2. Added basic sound feedback
3. Added slot level changes

Enclosure / CAD

1. Increased clearance around USB C connection

## Version 2.0 OFIs

Maker Guide

1. Test fit them into first holes first to get the leads aligned

# Appendix

## Resources

### Adafruit QT Py

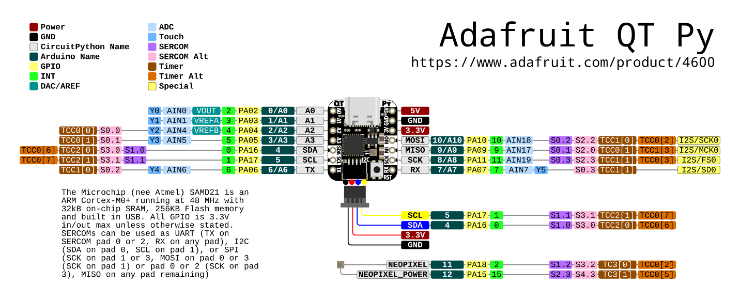
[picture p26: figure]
Adafruit QT Py SAMDI Pinout diagram

Figure 16. Adafruit QT Py Pinout. CC-BY-SA. https://learn.adafruit.com/assets/110643

© 2023-2024 by Neil Squire Society. This work is licensed under the CC BY SA 4.0 License: http://creativecommons.org/licenses/by-sa/4.0 Files available at https://github.com/makersmakingchange/Forest-Joystick-Mouse-Hub Page 1 of 1

V2.1 | APRIL 2024 Forest Hub Design Rationale

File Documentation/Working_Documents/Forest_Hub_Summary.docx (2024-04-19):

This document is intended to be a summary of a device to make it easier to add to the website.

# Product Information

## Product Name

Forest Joystick Mouse Hub

## Device Category

Adapted Toys

Aids for Daily Living (ADL)

Assistive Switches

Communication Aids (AAC)

Computer Access

Environmental Controls

Gaming

Keyguard

Kits

LipSyncs

Mounting

Recreation and Leisure

Seating and Positioning

Switch Interfaces

Writing Aids

## User Value Statement

Looking for an alternate way to control a mouse cursor

## Designer

Makers Making Change

# Device Info

## Overview

The OpenAT Forest Joystick Mouse Hub ("Forest Hub") enables a user to connect an analog joystick and one or more assistive switches to emulate a USB Mouse or USB Gamepad.

## Disability Type

Select one or more disability types:

Agility / Dexterity

Arthritis

Cognitive

Hearing

Mobility

Mobility

Other

Pain

SCI

Vision

## Disability Type Description

This is a key part of an access solution for those who have difficulty using traditional input devices like a computer mouse or gaming controller and may be especially useful for those with limited finger or hand dexterity.

## How To Use

First, the analog joystick and assistive switches are connected to the jacks located at the rear of the Hub. Next, the Hub is connected using the USB-C cable to a host device that supports USB Mouse or USB Gamepad.

In Mouse mode, moving the joystick will move the cursor in the corresponding direction. Activating the assistive switches will press the left mouse button, middle mouse button, right mouse button.

In Gamepad mode, the analog joystick maps to the gamepad joystick and the assistive switches map to the gamepad buttons.

The Hub has three different setting slots which can by cycled through by a short press on the Mode button or the Mode Switch jack. A long press on the Mode button or Switch attached to the Mode Switch Jack will toggle between Mouse mode and Gamepad mode..

## Estimated Cost

The estimated material cost of the device:

$0 - $10

$11 - $25

$26 - $50

$51 - $100

$101 - $250

$250+

## Attribution

- The Adafruit QT Py (http://www.adafruit.com/products/4600) development board was designed by Limor Fried/Ladyada from Adafruit. The PCB design is available open source (https://github.com/adafruit/Adafruit-QT-Py-PCB) under a CC-BY-SA license.
- The concept for the Forest Hub was based on the Enabled Controller Mini (https://github.com/milador/Enabled-Controller-Mini) by Milador.

# Maker Info

## Project Skills

3D Printing

Custom PCB

Electronics

Laser Cutting

Mechanics

Other

Software

Soldering

Woodworking

## Skills Description

<Maker-centric summary or additional details for the skills required to build the project>

## Tools Needed

3D Printer

Common Hand Tools

Common Power Tools

Laser Cutter

Soldering Iron

Specialized Tooling

## Print time (hrs)

4

## Assembly time (hrs)

1

## Build Instructions

This build consists of a number of off-the-shelf electronic components that are soldered into a custom PCB and assembled into a 3D printed enclosure. Firmware is then flashed to the microcontroller.

Detailed step-by-step instructions are available in the Maker Guide (https://github.com/makersmakingchange/Forest-Joystick-Mouse-Hub/blob/main/Documentation/Forest_Hub_Maker_Guide.pdf).

## Download Link

https://github.com/makersmakingchange/Forest-Joystick-Mouse-Hub/archive/refs/heads/main.zip

## Project Link

https://github.com/makersmakingchange/Forest-Hub

# License

## License

CERN OHL-W

Hardware: CERN OHL-W

Software:GPL 3+

Documentation: CC-BY-SA

© 2023 by Neil Squire Society. This work is licensed under the CC BY SA 4.0 License: http://creativecommons.org/licenses/by-sa/4.0 Files available at https://github.com/makersmakingchange/Forest-Joystick-Mouse-Hub Page 1 of 2

V1.0 | SEPTEMBER 2023 Forest Joystick Mouse Hub Summary

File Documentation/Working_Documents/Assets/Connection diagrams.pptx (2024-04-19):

## Connection diagrams for OpenAT Joysticks

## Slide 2

Forest Hub

Host device
(such as PC or mobile)

Assistive switches
(up to 4)

OpenAT Joystick

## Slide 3

Forest Hub
(Mouse Output Mode)

Host device
(such as PC or mobile)

Assistive switches
(up to 4)

OpenAT Joystick

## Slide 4

Host device
(such as smartphone or tablet)

Adapter

Forest Hub
(Mouse Output Mode)

Assistive switches
(up to 4)

OpenAT Joystick

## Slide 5


Host device
(such as smartphone or tablet)

Adapter with External Power

Forest Hub
(Mouse or Gamepad)

Assistive switches
(up to 4)

OpenAT Joystick

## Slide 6

Forest Hub
(Gamepad Output Mode)

Host device
(such as PC or mobile)

Assistive switches
(up to 4)

OpenAT Joystick

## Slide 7

Forest Hub
(Mouse or Gamepad)

Host device
(such as PC or mobile)

Assistive switches
(up to 4)

OpenAT Joystick

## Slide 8

Xbox Adaptive Controller

Host device
(such as PC, mobile, or Xbox)

Assistive switches
(up to 17)

OpenAT Joystick
(up to 2)

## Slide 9


Gaming Console (such as PlayStation, Nintendo Switch)

Adapter

Xbox Adaptive Controller

Assistive switches
(up to 17)

OpenAT Joystick
(up to 2)

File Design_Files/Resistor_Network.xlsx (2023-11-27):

R2 | 10000 |  | Rtop
R3 | 2200 |  | B2
R4 | 4700 |  | B1
R5 | 10000 |  | SW_M
Vs | 3.3
Case | SW_M | B1 | B2 | R_top | R_Bottom | V_Pin | ADC | Threshold
1 | 0 | 0 | 0 | 10000 | 16900 | 2.1 | 643
2 | 0 | 0 | 1 | 10000 | 14700 | 2.0 | 609 | 626 | t001
3 | 0 | 1 | 0 | 10000 | 12200 | 1.8 | 563 | 586 | t010
4 | 0 | 1 | 1 | 10000 | 10000 | 1.6 | 512 | 537.5 | t011
5 | 1 | 0 | 0 | 10000 | 6900 | 1.3 | 418 | 465 | t100
6 | 1 | 0 | 1 | 10000 | 4700 | 1.1 | 327 | 372.5 | t101
7 | 1 | 1 | 0 | 10000 | 2200 | 0.6 | 185 | 256 | t110
8 | 1 | 1 | 1 | 10000 | 0 | 0.0 | 0 | 92.5 | t111

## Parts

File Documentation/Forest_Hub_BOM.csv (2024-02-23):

 | Forest Joystick Mouse Hub |  |  |  |  |  |  |  | Total filament (g) | Unit Cost | Total Cost | Total Print time (hr)
 | Version: V2.0.2 | Last updated: | 2024-Feb-21 |  |  |  |  |  | 41 | $78.54 | $108.84 | 1:48
 | Commercial Parts
ID | Part | Description | Manufacturer | Supplier | Supplier PN | QTY/UNIT | QTY / PKG | PKGs | $/PKG | Price per Unit | Total Price |  | Link
 | Adafruit Qt PY SAMD21 | U1 | Adafruit | Mouser | 485-4600 | 1 | 1 | 1 | $10.88 | $10.88 | $10.88 |  | https://www.mouser.ca/ProductDetail/Adafruit/4600?qs=hd1VzrDQEGi752M4exorSA%3D%3D
 | Headers, Female, 7 Position | H1,H2 | Molex | Mouser | 90147-1107 | 2 | 1 | 2 | $2.41 | $4.82 | $4.82 |  | https://www.mouser.ca/ProductDetail/538-90147-1107
 | Mono Switch Jacks | SW_SA,SW_SB,SW_SC,SW_SD,SW_M | CUI Devices | Mouser | 490-SJ1-3535NG | 5 | 1 | 5 | $2.31 | $11.55 | $11.55 |  | https://www.mouser.ca/ProductDetail/CUI-Devices/SJ1-3535NG?qs=WyjlAZoYn50jUmKVsqeRJw%3D%3D
 | TRRS Jack | Joystick | CUI Devices | Mouser | 490-SJ-43514 | 1 | 1 | 1 | $1.91 | $1.91 | $1.91 |  | https://www.mouser.ca/ProductDetail/CUI-Devices/SJ-43514?qs=WyjlAZoYn51bsBOfuwwiuw%3D%3D
 | Tactile Buttons | B1,B2 | Omron | Mouser | 653-B3F-5050 | 2 | 1 | 2 | $0.90 | $1.80 | $1.80 |  | https://www.mouser.ca/ProductDetail/Omron-Electronics/B3F-5050?qs=dOLq8QE0Pqqk%2FO9x2OpTQw%3D%3D
 | Piezo Buzzer PS1240 | BUZZ | Adafruit | Mouser | 485-160 | 1 | 1 | 1 | 2.18 | $2.18 | $2.18 |  | https://www.mouser.ca/ProductDetail/Adafruit/160?qs=GURawfaeGuDIqfAvA4gXSg%3D%3D
 | Neopixels | L1,L2,L3,L4,L5 | Adafruit | Mouser | 485-1938 | 5 | 5 | 1 | $7.18 | $7.18 | $7.18 |  | https://www.mouser.ca/ProductDetail/Adafruit/1938?qs=GURawfaeGuAkVClyRWI8wg%3D%3D
 | Modular Connector (RJ25) | J1 | TE Connectivity / AMP | Mouser | 571-5555165-1 | 1 | 1 | 1 | $1.41 | $1.41 | $1.41 |  | https://www.mouser.ca/ProductDetail/TE-Connectivity-AMP/5555165-1?qs=BcfjnG7NVaWb2UIqidZ6Zg%3D%3D
 | Resistor, 220, 1/4W, Through hole | R1 | KOA Speer | Mouser | 660-MF1/4LCT52R221J | 1 | 1 | 1 | $0.15 | $0.15 | $0.15 |  | https://www.mouser.ca/ProductDetail/KOA-Speer/MF1-4LCT52R221J?qs=91WPSIiQh9JIjB%2FAtwkZiw%3D%3D
 | Resistor, 2.2K, 1/4W, Through hole | R3 | KOA Speer | Mouser | 660-MF1/4LCT52R222G | 1 | 1 | 1 | $0.15 | $0.15 | $0.15 |  | https://www.mouser.ca/ProductDetail/KOA-Speer/MF1-4LCT52R222G?qs=91WPSIiQh9Kh6m%2FGxJ5MCA%3D%3D
 | Resistor, 4.7K, 1/4W, Through Hole | R4 | KOA Speer | Mouser | 660-MF1/4LCT52R472G | 1 | 1 | 1 | $0.15 | $0.15 | $0.15 |  | https://www.mouser.ca/ProductDetail/KOA-Speer/MF1-4LCT52R472G?qs=91WPSIiQh9K2asC3F9ek6A%3D%3D
 | Resistor, 10K, 1/4W, Through hole | R2,R6 | KOA Speer | Mouser | 660-MF1/4LCT52R103J | 2 | 1 | 2 | $0.15 | $0.29 | $0.29 |  | https://www.mouser.ca/ProductDetail/KOA-Speer/MF1-4LCT52R103J?qs=DG1n8gfZNTsQyNkYIaO24A%3D%3D
 | Resistor, 100, 1/4W, Through hole | R5 | KOA Speer | Mouser | 660-MF1/4LCT52R101J | 1 | 1 | 1 | $0.15 | $0.15 | $0.15 |  | https://www.mouser.ca/ProductDetail/KOA-Speer/MF1-4LCT52R101J?qs=DG1n8gfZNTsgm1lQXnAQZw%3D%3D
 | Capacitor, 10 uF | C1 | KEMET | Mouser | 80-C430C106K3R5TA | 1 | 1 | 1 | $1.00 | $1.00 | $1.00 |  | https://www.mouser.ca/ProductDetail/KEMET/C430C106K3R5TA?qs=QTajy0ParP4Iyid6Jgh%2FcQ%3D%3D
 | Screw, #4, Self-tapping, 3/8? Length | Screw |  | Mouser | 635-6005 | 1 | 1 | 1 | $0.49 | $0.49 | $0.49 |  | https://www.mouser.ca/ProductDetail/SERPAC/6005?qs=f95KBKa1t%252BoPqs5qKc4pog%3D%3D
 | USB-C Cable | USB-C | Adafruit | Mouser | 485-4474 | 1 | 1 | 1 | $7.18 | $7.18 | $7.18 |  | https://www.mouser.ca/ProductDetail/Adafruit/4474?qs=CUBnOrq4ZJz9F%2FNF%252BRRALQ%3D%3D
 | Mouser Shipping |  |  | Mouser |  | 1 | 1 | 1 | $20.00 | $20.00 | $20.00
 | Custom PCB
 | Part | Description | Manufacturer | Supplier | Supplier PN | QTY | QTY / PKG | PKG | $/PKG | Price per Unit | Total Price |  | Link
 | Forest Hub PCB | PCB | JLCPCB |  |  | 1 | 5 | 1 | $12.26 | $2.45 | $12.26
 | PCB Shipping | PCB Shipping - Rush |  |  |  | 0 | 5 | 0 | $40.33 | $- | $-
 | PCB Shipping | Fedex International |  |  |  | 1 | 5 | 1 | $24.07 | $4.81 | $24.07
 | PCB Shipping
 | 3D Printed Parts ESTIMATED PRICING USING 1KG ROLL COST: | $30.00
 | Part | Description |  |  |  | QTY | Mass (g) |  | Estimated Price/part | Price Per Unit | Total Price | Print Time (hr:Min) | Link
 | Forest Enclosure Top | Forest_Enclosure_Top.stl |  |  |  | 1 | 25 |  | $0.75 | $0.75 | $0.75 | 0:36
 | Forest Enclosure Bottom | Forest_Enclosure_Bottom.stl |  |  |  | 1 | 13 |  | $0.39 | $0.39 | $0.39 | 1:12
 | Forest LED Spacer | Forest_LED_Spacer.stl |  |  |  | 1 | 3 |  | $0.09 | $0.09 | $0.09
 | Alternatives
 | Part | Description | Manufacturer | Supplier
 | Screw, #4, 3/8" Length |  |  | Amazon |  | 1 | 100 | 1 | $9.30 | $0.09 | $9.30 |  | https://a.co/d/523bJeL
 | Adafruit QT Py RP2040 | U1 Alt | Adafruit | Mouser | 485-4900 | 1 | 1 | 1 | $14.43 | $14.43 | $14.43
 | Neopixels | L1,L2,L3,L4,L5 | Adafruit | Digikey | 1528-1959-ND | 5 | 5 | 1 | $7.18 | $7.18 | $7.18 |  | https://www.digikey.ca/en/products/detail/adafruit-industries-llc/1938/6827082?s=N4IgTCBcDaIKwFsEAIB2BTA9gBwJYA90AbEAXQF8g

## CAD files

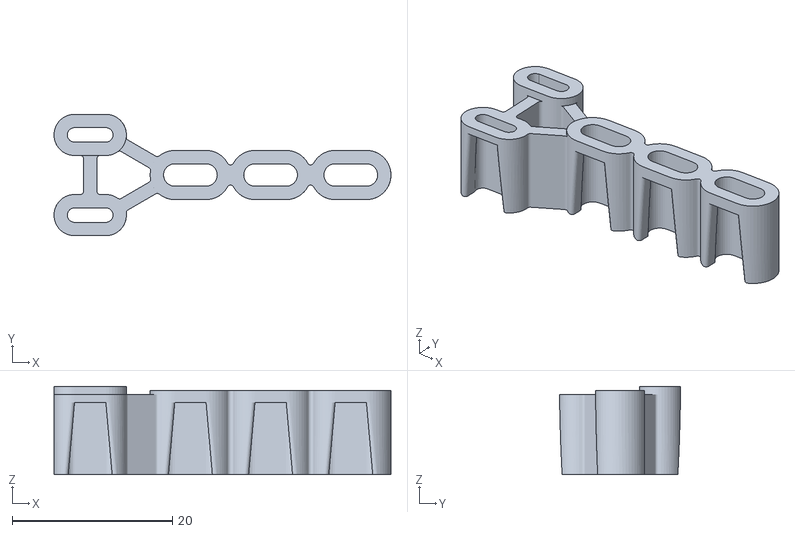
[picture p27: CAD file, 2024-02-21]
Build_Files/3D_Printing_Files/Forest_LED_Spacer.stl
42.0 x 15.1 x 11.0

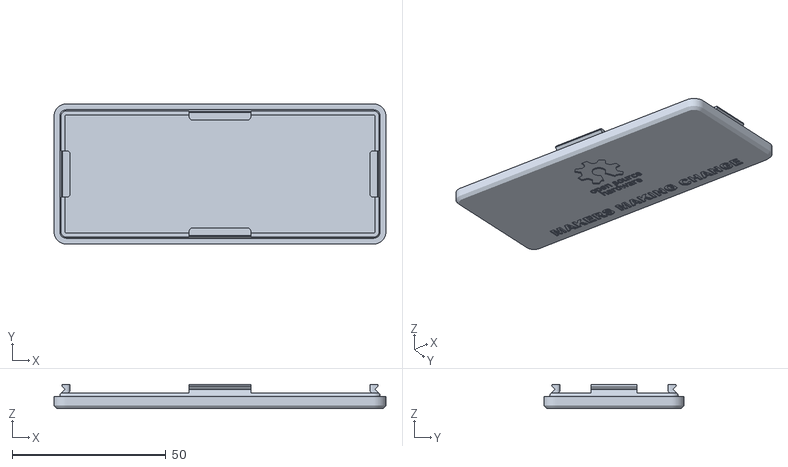
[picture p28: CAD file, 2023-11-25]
Build_Files/3D_Printing_Files/Forest_Hub_Bottom.stl
107.8 x 45.5 x 7.87

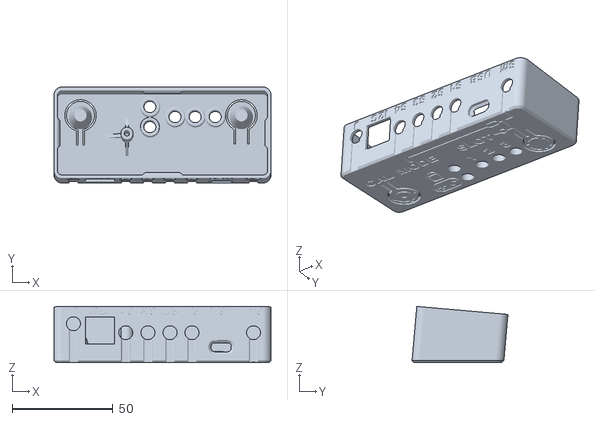
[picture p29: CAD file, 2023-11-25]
Build_Files/3D_Printing_Files/Forest_Hub_Top.stl
107.8 x 47.7 x 27.9

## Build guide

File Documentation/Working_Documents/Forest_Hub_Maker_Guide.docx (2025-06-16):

# Overview

This document contains the necessary information to build the device.

# Maker Checklist

This list provides an overview of the steps required to build and deliver the device.

## Maker To Do List

- Read through the Assembly Guide to become familiar with required components, tools, supplies, and safety gear and overall assembly steps.
- Talk to User about customization options (e.g., colour, any special requests, etc.)
- Ask user if any assistive switches are required.
- Ask user if any analog joysticks are required.
- Estimate cost of materials
- Order the custom PCB
- Order hardware components
- Print or obtain the 3D prints
- Gather tools, supplies, and safety equipment.
- Assemble the device
- Test device
- Print “User Guide”

## Items to Give to User

- Assembled, tested device
- “User Guide”

# Tool List

1. Soldering iron
2. Flush cutters
3. Phillips Head Screwdriver
4. Computer with USB port and Arduino IDE (or ability to install it)

# Customization Guide

The device can be printed in the user’s desired color.

## Contrasted Labels

A layer change can be done for the top and bottom enclosure to make the labels have greater contrast.

## Colored Labels

If you have access to a suitable multiple extruder or multiple color 3D printer, the labels can be printed in multiple colors.

# Custom PCB Guide

The Forest Hub uses one (1) custom circuit board.

The Custom PCB can be ordered from one of a variety of PCB Manufacturers. Typically, the minimum quantity for a custom PCB is five. Shipping options vary significantly in cost and shipping time. Plan on at least a week from the time of order to the PCBs arrival.

## Ordering the Custom PCB

1. Select a PCB Fabrication Company
  a. JLPCB (https://jlcpcb.com/)
  b. PCBWay (https://www.pcbway.com/)
  c. OSH Park (https://oshpark.com/)
  d. Seeed Fusion PCB (https://www.seeedstudio.com/fusion_pcb.html)
2. Create an account or use a guest login.
3. Upload the Gerber Files (e.g., Forest-Joystick-Mouse-Hub_YYY-MM-DD.zip).
4. Select the fabrication options:
  a. PCB Layers: 2 Layers
  b. PCB Quantity: 5
  c. PCB Thickness: 1.5 mm
  d. Surface Finish: HASL
  e. PCB Color: Choose what you like. Note that certain colors may impact build time.
  f. The default settings for the other settings should work.
5. Select shipping option.
  a. Shipping options and costs vary significantly. Select the best option based on your budget and timing.
6. Submit the order.

# 3D Printing Guide

## 3D Printing Summary

Metrics | Single Unit
Total Print Time (min) | 3h52m
Total Number of Components | 3
Typical Total Mass (g) | 40
Typical Number of Print Setups | 1

## 3D Printing Settings

Print File Name | Qty | Total Print Time (hr:min) | Mass (g) | Infill (%) | Support(Y/N) | Layer Height/ Nozzle Diameter(mm) | Notes
Forest_Hub_Top.stl | 1 | 2:40 | 24 | 15 | N | 0.2/0.4
Forest_Hub_Bottom.stl | 1 | 0:51 | 13 | 15 | N | 0.2/0.4
Forest_HUB_LED_Spacer.stl | 1 | 0:20 | 3 | 15 | N | 0.2/0.4

## Post-Processing

- Remove any stringing or blobs

## Examples of Quality Prints

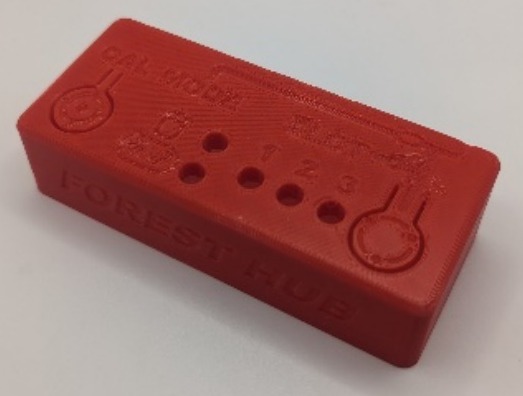
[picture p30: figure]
Okay quality Forest Hub Top
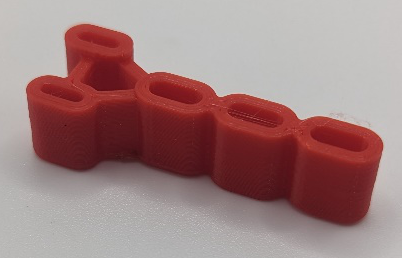
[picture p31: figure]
A photo of the Forest LED Spacer printed in red PLA on a white background.

# Assembly Guide

The assembly of the Forest Hub is comprised of three parts:

1. Part A: PCB Assembly
2. Part B: Firmware
3. Part C: Enclosure Assembly

## Part A: PCB Assembly

### Part A Components

1 | | Forest Hub PCB | QTY 1 | | 2 | Capacitor, 10uF | | QTY 1 | | 3 | Resistor R1, 220Ω | | | | QTY 1
4 | | Resistor R3, 2.2KΩ | QTY 1 | | 5 | Resistor R4, 4.7KΩ | | QTY 1 | | 6 | Resistor R2/R6, 10KΩ | | | | QTY 2
7 | | Resistor R5, 100Ω | QTY 119 | | 8 | Tactile Buttons | | | QTY 2 | 9 | | | Piezo Buzzer PS1240 | | QTY 1

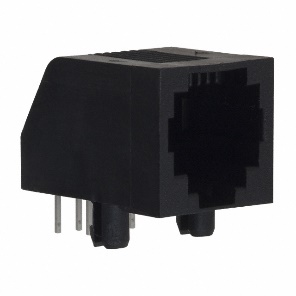
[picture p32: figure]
A RJ11 jack

10 | | TRRS Jack | | 1 QTY 19 | 11 | Mono Switch Jacks | QTY 519 | | | 12 | | Modular Connector (RJ25) | | QTY 119
13 | | Adafruit Qt PY SAMD21 | | QTY 1 | 14 | Headers, Female, 7 Position | QTY 2 | | | 15 | | NeoPixel LEDs, 5 mm though hole | | QTY 5

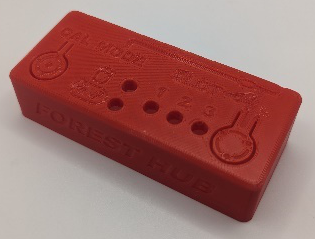
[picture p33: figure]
A photo of the Forest enclosure top printed in red PLA on a white background.

16 | | Forest LED Spacer | | QTY 1 | 17 | Forest Enclosure Top | QTY 1 | | | 18 | | Screw, #4, 3/8” Length | | QTY 1

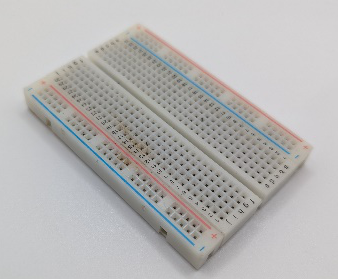
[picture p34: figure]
A photo of a solderless breadboard on a white background.

19 | Forest Enclosure Bottom | | | QTY 1 | 20 | USB-C Cable | QTY 1 | | | 21 | | Solderless Breadboard | | QTY 1

### Part A Tools

- Soldering iron
- Flush cutters
- Phillips Head Screwdriver

### Part A Personal Protective Equipment (PPE)

- Safety glasses

### Part A Steps

#### Step 1: Insert and Solder Capacitor

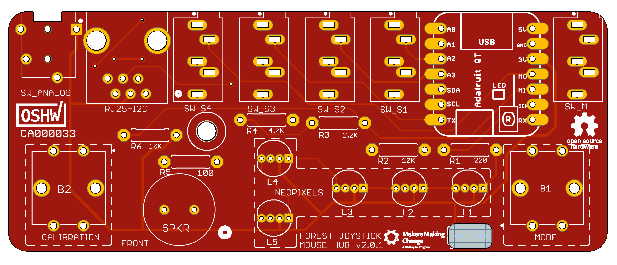
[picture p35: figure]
PCB screenshot showing C1 location

Take the capacitor and bend the metal leads on either side so they will line up with the holes labelled C1 on the PCB. Insert the capacitor leads all the way into the C1 holes. Solder in place and trim the excess leads off.

#### Step 2: Insert and Solder R1 Resistor

Take the R1 resistor (220 Ω) and bend the metal leads on either side so they will line up with the holes labelled R1 on the PCB. Insert the resistor leads all the way into the R1 holes. Flip the board to the back, solder in place and trim the excess leads off.

#### Step 3: Insert and Solder R2 Resistor

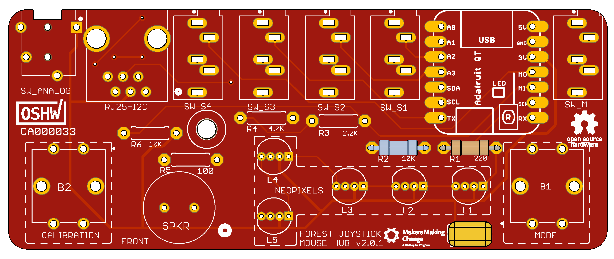
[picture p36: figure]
PCB screenshot showing R2 location

Take the R2 resistor (10KΩ) and bend the metal leads on either side so they will line up with the holes labelled R2 on the PCB. Insert the resistor leads all the way into the R2 holes. Flip the board to the back, solder in place and trim the excess leads off.

#### Step 4: Insert and Solder R3 Resistor (Component 4)

Take the R3 resistor (2.2KΩ) and bend the metal leads on either side so they will line up with the holes labelled R3 on the PCB. Insert the resistor leads all the way into the R3 holes. Solder in place and trim the excess leads off.

#### Step 5: Insert and Solder R4 Resistor (Component 5)

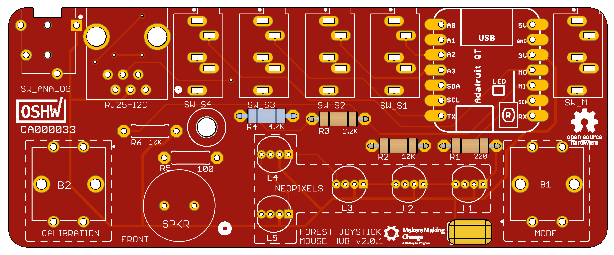
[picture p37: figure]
PCB screenshot showing R4 location

Take the R4 resistor (4.7KΩ) and bend the metal leads on either side so they will line up with the holes labelled R4 on the PCB. Insert the resistor leads all the way into the R4 holes. Solder in place and trim the excess leads off.

#### Step 6: Insert and Solder R5 Resistor (Component 7)

Take the R5 resistor (100Ω) and bend the metal leads on either side so they will line up with the holes labelled R5 on the PCB. Insert the resistor leads all the way into the R5 holes. Solder in place and trim the excess leads off.

#### Step 7: Insert and Solder R6 Resistor (Component 6)

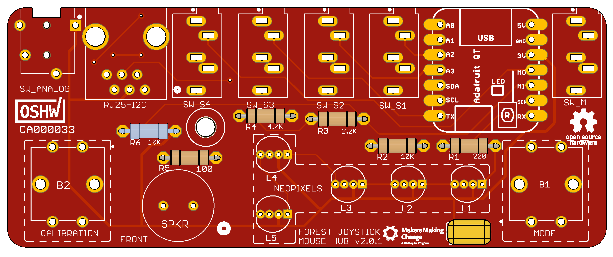
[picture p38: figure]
PCB screenshot showing R6 location

Take the R6 resistor (10KΩ) and bend the metal leads on either side so they will line up with the holes labelled R6 on the PCB. Insert the resistor leads all the way into the R6 holes. Solder in place and trim the excess leads off.

#### Step 8: Insert and Solder Buzzer

Take the Buzzer (Component 9) and insert the leads all the way into the PCB holes labelled with a speaker icon from the top. Solder in place and trim the excess leads.

#### Step 9: Insert and Solder Calibration Button

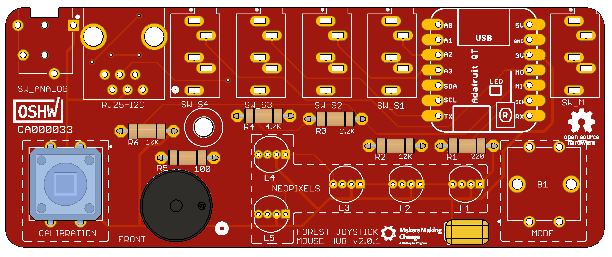
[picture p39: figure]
PCB screenshot showing Calibration Button location

Take a button (Component 8) and insert the leads all the way into the PCB holes labelled CALIBR from the top. Solder a single pin, check that the component is fully flush to the PCB, and solder the remaining pins.

#### Step 10: Insert and Solder Mode Button

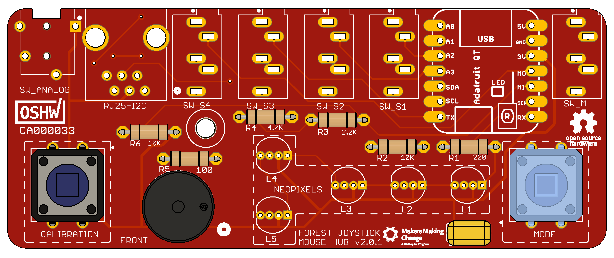
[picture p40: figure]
PCB screenshot showing Mode Button location

Take a button (Component 8) and insert the leads all the way into the PCB holes labelled Mode from the top. Solder a single pin, check that the component is fully flush to the PCB, and solder the remaining pins.

#### Step 11: Insert and Solder TRRS Jack

Take the TRRS jack (Component 10) and insert the leads all the way into the PCB holes labelled SW_ANALOG from the top. Solder a single pin, check that the component is fully flush to the PCB, and solder the remaining pins.

#### Step 12: Insert and Solder SM Audio Jack

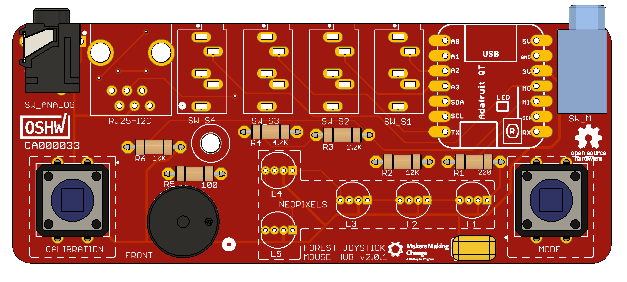
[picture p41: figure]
PCB screenshot showing SM jack location

Take an audio jack (Component 11) and insert the leads all the way into the PCB holes labelled SW_M from the top. Solder a single pin, check that the component is fully flush to the PCB, and solder the remaining pins.

#### Step 13: Insert and Solder S1 Audio Jack

Take an audio jack (Component 11) and insert the leads all the way into the PCB holes labelled SW_S1 from the top. Solder a single pin, check that the component is fully flush to the PCB, and solder the remaining pins.

#### Step 14: Insert and Solder S2 Audio Jack

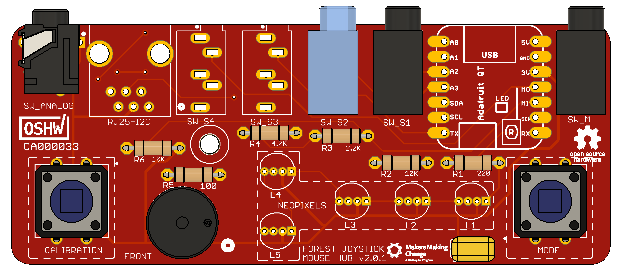
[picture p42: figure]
PCB screenshot showing S2 jack location

Take an audio jack (Component 11) and insert the leads all the way into the PCB holes labelled SW_S2 from the top. Solder a single pin, check that the component is fully flush to the PCB, and solder the remaining pins.

#### Step 15: Insert and Solder S3 Audio Jack

Take an audio jack (Component 11) and insert the leads all the way into the PCB holes labelled SW_S3 from the top. Solder a single pin, check that the component is fully flush to the PCB, and solder the remaining pins.

#### Step 16: Insert and Solder S4 Audio Jack

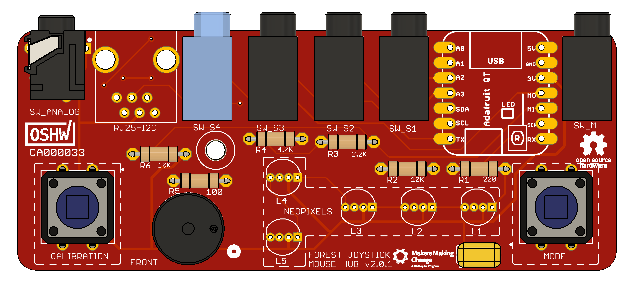
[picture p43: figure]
PCB screenshot showing S4 jack location

Take an audio jack (Component 11) and insert the leads all the way into the PCB holes labelled SW_S4 from the top. Solder a single pin, check that the component is fully flush to the PCB, and solder the remaining pins.

#### Step 17: Insert and Solder Male Headers to QT Py

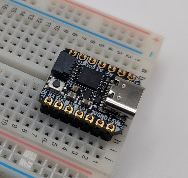
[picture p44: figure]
Solderless breadboard with two 7 position male headers and Qt Py
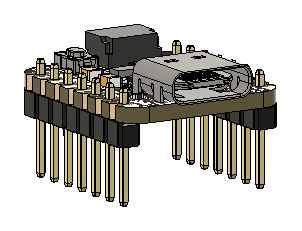
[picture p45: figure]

Take the QT Py microcontroller and male headers (Component 13). If necessary, use the flush cutters to separate the male headers into two 7 position segments. If you have a solderless breadboard: - Insert the long leads of the male headers into the breadboard and insert the microcontroller on top. Solder the pins in place and remove the assembly.
If you do not have a solderless breadboard: - Insert the male headers into the microcontroller board. - Use the female heads rotated 90 degrees to provide the correct spacing. - Solder a single male header pin to the microcontroller, ensuring the headers are perpendicular to the PCB and the microcontroller is parallel with the PCB. - Check that the male headers are flush and perpendicular to the microcontroller, solder the remaining male headers pins in place.

#### Step 18: Insert and Solder Female Headers

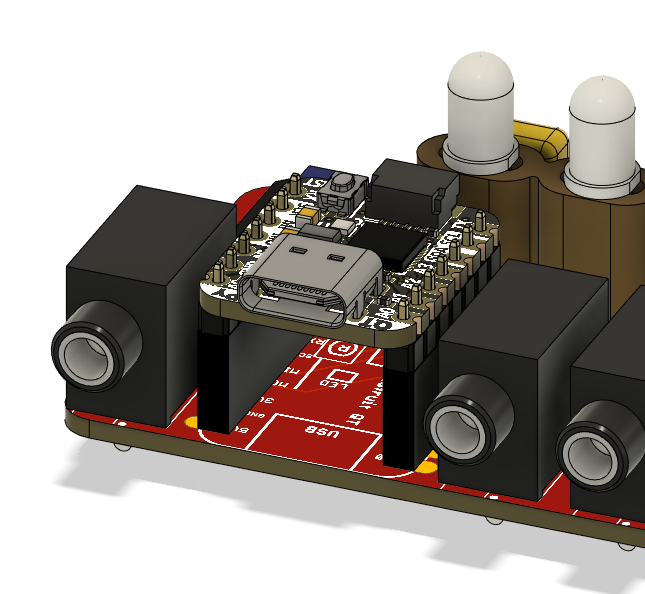
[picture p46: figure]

Insert the male headers into the female headers (Component 14) and insert the female headers into the PCB holes outlined with the microcontroller footprint from the top. Solder a single pin of one female header and check to ensure the female headers are flush and perpendicular with the PCB. Solder the remaining female header pins.

#### Step 19: Insert and Solder RJ25 Connector

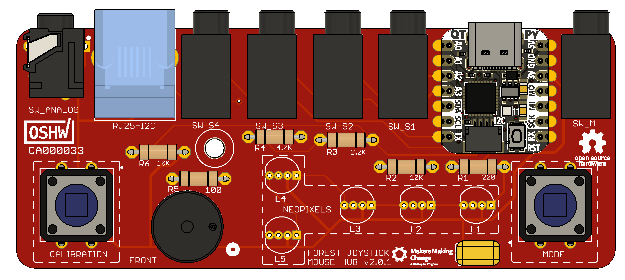
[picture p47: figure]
PCB screenshot showing RJ25 jack location

Take the RJ25 Modular connector and insert it into the PCB holes located between SW_S4 and SW_ANALOG. Solder a single pin, check that the component is fully flush to the PCB, and solder the remaining pins.

#### Step 20: Space out NeoPixel LED Leads by Inserting into PCB

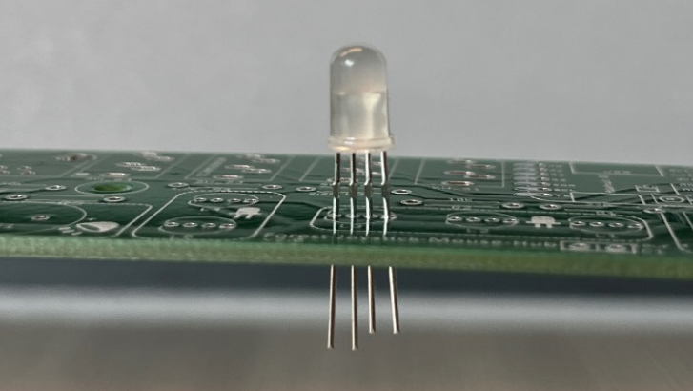
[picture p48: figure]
NeoPixel LED inserted into green circuit board.

Insert each of the NeoPixel LEDs into the PCB to correctly space out the NeoPixel leads, then remove the NeoPixels from the PCB. This will make the next step less difficult. The longer leads should be oriented towards the left.

#### Step 21: Insert NeoPixel LEDs using Forest LED Spacer

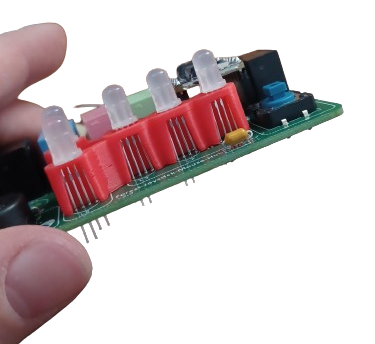
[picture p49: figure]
NeoPixel LEDs inserted into PCB through 3D printed spacer

Take the NeoPixel LEDs (Component 15) and the Forest LED spacer (Component 16). Line up and place the spacer over the PCB holes labelled L1, L2, L3, L4, and L5. Ensuring that the flat side of the NeoPixel LEDs lines up with the outline on the PCB (all LED flat sides should face towards the Buzzer), insert the LEDs into the PCB. The longer leads should be oriented towards the left. If needed, use a small tool such as a toothpick to guide the leads into the PCB. Solder in place and trim the excess leads.

#### Step 22: Doublecheck LED soldering

Visibly check for solder bridges (solder going between and connecting the pads) on the pads for the NeoPixels LEDs. If there are any, remove the connecting solder.

#### Step 23: PCB is Fully Assembled

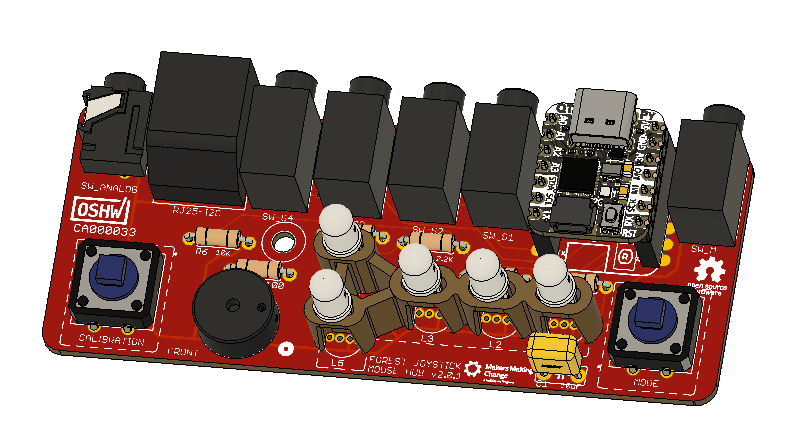
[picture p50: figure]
Assembled PCB

The Forest Hub PCB is now fully assembled. Move to Part B: Firmware.

## Part B: Firmware

### Part B: Firmware Steps

#### Step B1: Setup Arduino IDE

1. Download Arduino IDE for your operating system at https://www.arduino.cc/en/software
2. Install the Arduino IDE.

#### Step B2: Setup Arduino IDE for QT Py Board

1. Open Arduino IDE.
2. Click on File -> Preferences.
3. Locate the text field that says Additional Boards Manager URLs beside it.
4. Copy and paste the following link into the field as a new line: https://adafruit.github.io/arduino-board-index/package_adafruit_index.json
5. Click on OK.
6. Restart the Arduino IDE.
7. Open the Boards Manager option from the Tools-> Board-> Boards Manager...,
8. Search for “Adafruit SAMD” and select “Adafruit SAMD Boards” by Adafruit.
9. Click Install to install the board.

#### Step B3: Install Libraries

1. In a web browser, go to https://github.com/cyborg5/TinyUSB_Mouse_and_Keyboard and go to Code -> Download ZIP.
2. In Arduino IDE, click Sketch -> Include Library -> Add .ZIP Library.
3. Navigate to the ZIP file downloaded in Step (a). Click OK.
4. Go to Tools -> Manage Libraries…, search for “Flash Storage” and install the library “FlashStorage” by Various.
5. Go to Tools -> Manage Libraries…, search for “Adafruit_Neopixel” and install the library “Adafruit_Neopixel” by Adafruit.
6. Go to Tools -> Manage Libraries…, search for “WiiChuck” and install the library “WiiChuck” by Kevin Harrington.

#### Step B4: Setup Local Code Directory

1. Download the Firmware_Files from the GitHub Repository: https://github.com/makersmakingchange/Forest-Hub/blob/main/Build_Files/Firmware_Files/Forest_Hub_Firmware.zip
2. Extract / unzip the folder to a known location.
3. Confirm that you have the following folder structure:
- Forest_Hub_Firmware (folder)
  - Forest_Hub_Firmware.ino
  - OpenAT_Joystick_Response.h
  - XACGamepad.h

#### Step B5: Upload the Code to the microcontroller

1. Open Forest_Hub_Firmware.ino with Arduino IDE.
2. Select Adafruit QT Py M0 (SAMD21) from Tools -> Board -> Adafruit SAMD Boards
3. Click on Tools -> USB Stack and select TinyUSB
4. Connect the Forest Hub using the USB cable to the computer.
5. Select the correct port from Tools -> Port menu.
6. Verify and upload the code.

## Part C: Enclosure Assembly

### Part C Components

22 | Assembled Forest Hub PCB | QTY 1 | | 17 | Forest Enclosure Top | | QTY 1 | 18 | Screw, #4, 3/8” Length | | | QTY 1
19 | Forest Enclosure Bottom | | QTY 1 | 20 | USB-C Cable | QTY 1

### Part C Steps

#### Step C1: Insert PCB into Enclosure Top

Insert the assembled PCB into the Enclosure Top.

#### Step C2: Secure PCB into place with Screw

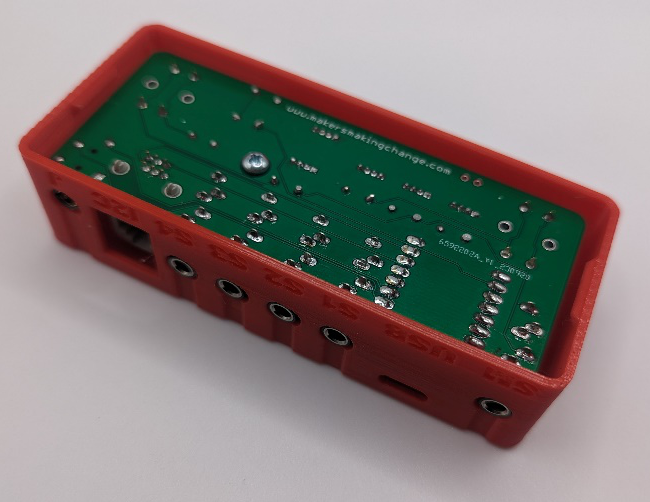
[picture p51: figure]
A screw used to affix PCB into enclosure

Secure the PCB in place with using the #4 screw and the Phillips screwdriver.

#### Step C3: Snap Enclosure Bottom

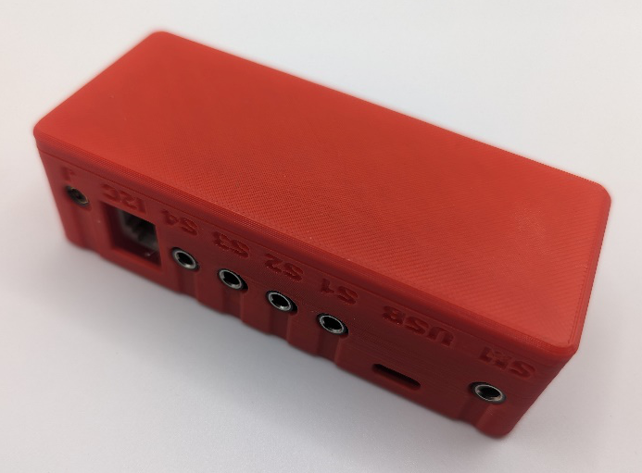
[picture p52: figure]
Top enclosure with bottom enclosure snap-fit

Position the Enclosure Bottom over the Enclosure Top and push down to snap in place.

#### Step C4: Enclosure Finished

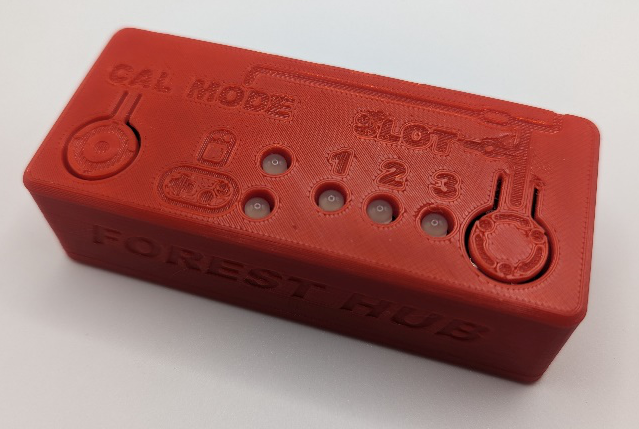
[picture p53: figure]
Finished Forest Hub Enclosure

Flip the device over. The Forest Hub is now complete.

# Testing

To test the Forest Hub, you will need an analog joystick and at least one (1), but up to preferably five (5) assistive switches.

## Testing using a PC

1. Connect the joystick using the USB C cable to the computer.
2. If the Forest is in mouse mode, change to gamepad mode (long press of Mode/Slot button).
3. If using Windows, open “Set up USB Game Controllers” from the Control Panel. You can find this by searching your computer in the search bar next to the Windows icon.
4. Ensure that the joystick is registered as a game controller and select your joystick from the list and go to “Properties”.
5. Move your joystick and observe the movement of the cross hatch in the “Axes” window. Ensure it moves in the proper directions when you move the joystick (the arrow points in the up direction). If not, open the joystick and check your connections.
6. Using assistive switches plugged into each mono jack, activate each switch, and ensure that one of buttons 1-4 light up when you press the switch, and stops when you release the switch. If not, open the joystick and check your connections.

## Testing using an Xbox Adaptive Controller

1. Connect the Forest Hub into the Left USB port for the left joystick or the Right USB port for the right joystick.
2. Connect the Xbox Adaptive Controller (XAC) using a USB-C cable to the computer.
3. If the Forest is in mouse mode, change to gamepad mode (long press of Mode/Slot button).
4. If using Windows, open “Set up USB Game Controllers” from the Control Panel. You can find this by searching your computer in the search bar next to the Windows icon.
5. Select the Xbox Adaptive Controller from the list of controllers and go to “Properties”.
6. Move your joystick and observe the movement of the cross hatch in the “Axes” window. Ensure it moves in the proper directions when you move the joystick (the arrow points in the up direction). If not, open up the joystick and check your connections.

# Troubleshooting

Nothing happens when I plug the device in.

- Double check to make sure there are no bridged connections. Double check the Neopixels and the RJ11 Connector.

© 2023-2024 by Neil Squire Society. This work is licensed under the CC BY SA 4.0 License: http://creativecommons.org/licenses/by-sa/4.0 Files available at https://github.com/makersmakingchange/Forest-Joystick-Mouse-Hub Page 1 of 24

V2.1 | APRIL 2024 Forest Joystick Mouse Hub maker Guide

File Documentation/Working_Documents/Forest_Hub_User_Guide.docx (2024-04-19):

# Introduction

The Forest Joystick Mouse Hub allows you to connect an analog joystick and up to four (4) assistive switches to use as a USB HID Mouse or USB HID Gamepad. An additional assistive switch can be used to cycle between 3 slots and switch between Mouse mode and Gamepad mode.

# Features

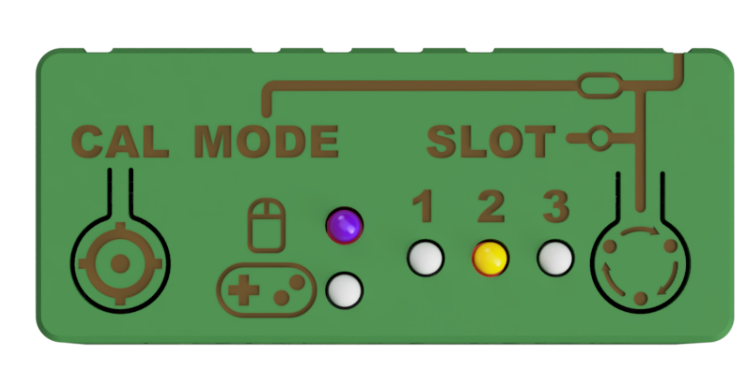
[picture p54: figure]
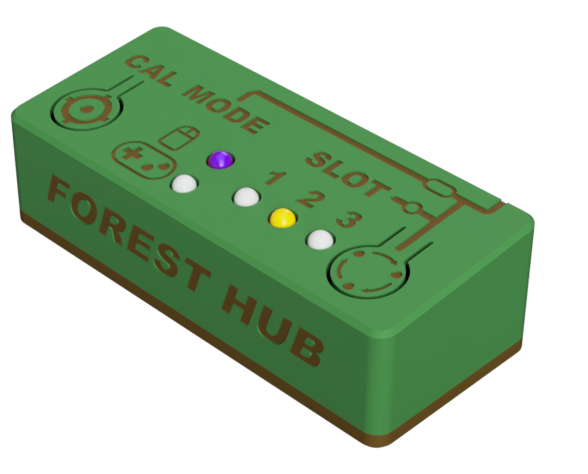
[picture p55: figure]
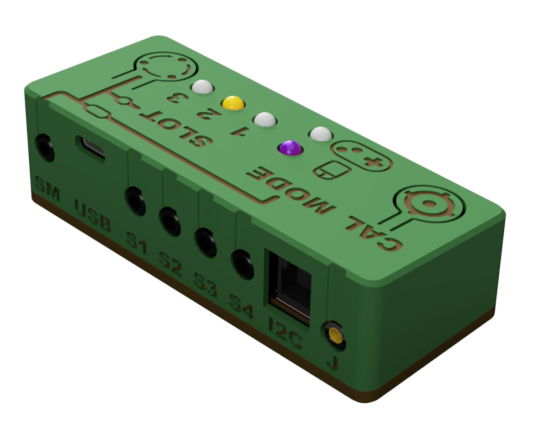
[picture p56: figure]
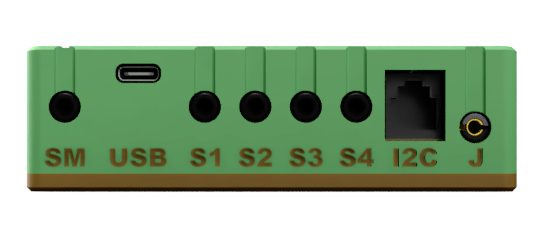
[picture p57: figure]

Calibration button

Mode Button

Output Mode Indicators

Slot Indicator

Mode Switch Port

Assistive Switch Ports

USB Port

Joystick Port

# Setting Up the Forest Hub

## Compatible Joysticks

The Forest Hub is compatible with any analog joystick that is designed to also work on the Xbox Adaptive Controller or Sony Access Controller. The connector on an analog joystick looks like a 4-conductor headphone jack (i.e. TRRS), as pictured below:

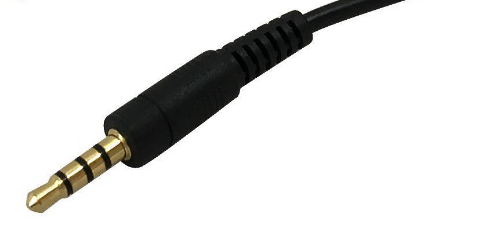
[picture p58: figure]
3.5mm (1/8 inch) 4C TRRS male to male 28AWG FT4 Cable - Black

Some examples of analog joysticks made by Makers Making Change include the Oak Compact Joystick (https://www.makersmakingchange.com/s/product/oak-compact-joystick/01tJR00000092x3YAA), the Spruce Mini Joystick (https://www.makersmakingchange.com/s/product/spruce-mini-joystick/01tJR000000EHqbYAG), and the Birch Mini Joystick. (https://www.makersmakingchange.com/s/product/birch-mini-joystick/01tJR0000009357YAA)

## Setup

1. Connect an analog joystick to the Joystick port (J).
2. Connect assistive switches to the Switch Input ports (S1, S2, S3, S4).
3. Connect an additional assistive switch to the Slot/Mode Input port (SM).
4. Connect the USB-C cable to the Hub, then to the Host Device.
5. Wait until the slot indicator light turns on, and the buzzer beeps to indicate mode and slot number, before moving the joystick.

## Connecting to Host Device

### Host Device Compatibility

- USB HID Mouse: PC, Mac, Android Smartphone, Apple Smartphone (iOS 13+)
- USB HID Gamepad: PC, Xbox Adaptive Controller

### Plugging Directly into a Computer or Laptop

If you have the appropriate cable, the Forest Hub can be directly plugged into the device’s USB port to work in Mouse or Gamepad mode. The Forest Hub port requires a USB-C plug, and most host devices will require either USB-A or USB-C plug types.

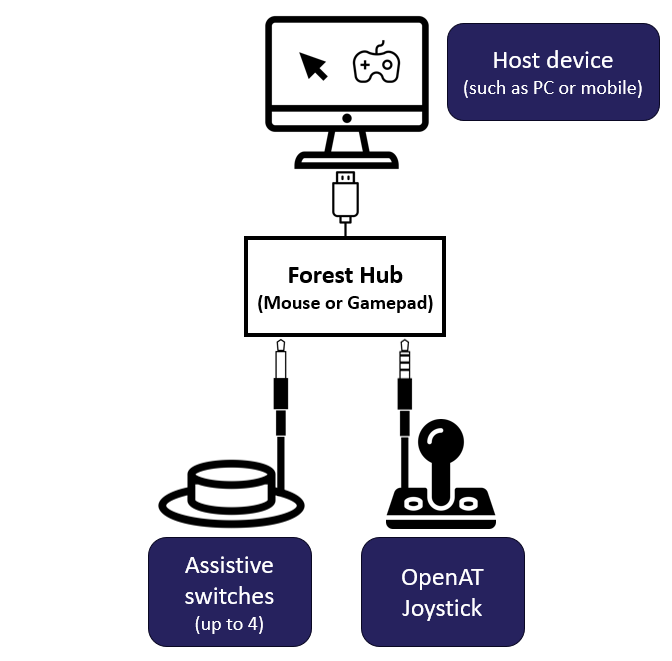
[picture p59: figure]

### Plugging Directly into an Android Mobile Phone or Tablet

The Forest Hub can be directly plugged into the device’s USB port to work in Mouse or Gamepad mode using the appropriate cable and/or adapter. The Forest Hub port requires a USB C plug, and most host devices will require either USB-C, USB-B Micro, or USB-A plug types.

### Plugging into an iOS or Android Mobile Device with an External Power Source

The Forest Hub cannot draw power from an iOS device, and therefore must have a powered USB hub or powered USB splitter to connect between the Forest Hub and iOS device. For an Android mobile device (phone or tablet), using an external power source is optional, but can extend the battery life of your device.

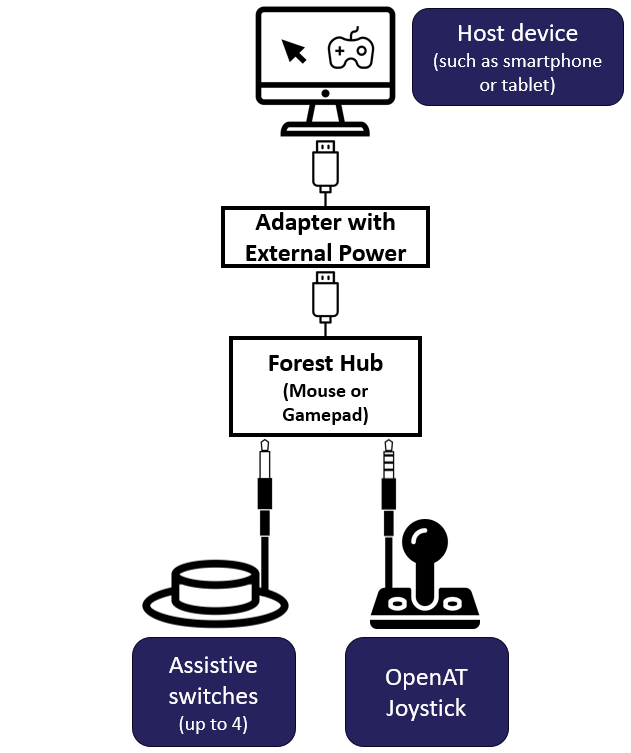
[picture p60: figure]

# Operating the Forest Hub

The Forest Hub is able to operate in two modes: Mouse Mode and Gamepad Mode.

- In Mouse Mode, the joystick controls the movement of the mouse cursor and the assistive switches are mapped to different mouse buttons.
- In Gamepad Mode, the joystick controls the analog movement of the gamepad joystick and the assistive switches are mapped to different gamepad buttons.

## Forest Hub Controls Mapping

### Device Controls

Input | Mouse (PC or Mobile) | Gamepad
| | PC | Mobile (Android) | XAC (Left USB) | XAC (Right USB)
Joystick | Cursor movement | Joystick movement | Directional pad | Left Thumbstick | Right Thumbstick
S1 | Left click | Button 1 | Select | X1 (Left Stick Up) | View
S2 | Middle Click | Button 2 | Back | X2 (Left Stick Down) | Menu
S3 | Right Click | Button 3 | Select | Left Stick Press | Right Stick Press
S4 | Toggle Scroll On/Off | Button 4 | N/A | Left Bumper | Right Bumper

### Hub Settings Controls

Input | Mouse or Gamepad
| Short Press | Long Press
SM Switch | Cycle Slot | Change Mode
Mode Button | Cycle Slot | Change Mode
Calibration Button | Center Reset | --

## Mouse Mode Controls

The Forest Hub is able to simulate most basic mouse functions, including mouse movement, left click, middle click, right click, and scroll.

### Mouse Movement

To move the mouse, move your joystick in the desired direction. Ensure your joystick is oriented properly. The amount you move the joystick correlates to the mouse speed, so moving the joystick further in one direction will move it faster.

### Mouse Clicks

For left click, middle click, and right click, while the corresponding assistive switch is pressed the mouse function will be pressed, and will be held until the assistive switch is released. Left click is conducted by activating assistive switch S1, middle click by activating assistive switch S2, and right click by activating assistive switch S3.

### Mouse Scroll

To simulate a mouse scroll wheel, press assistive switch S4 to enter scroll mode, and while in scroll mode, move the joystick up or down in the desired scroll direction. To exit scroll mode, press assistive switch S4 again. Note that moving the joystick left or right will not scroll sideways, to scroll sideways try either using middle click or using arrows on the screen.

When entering scroll mode, the mode LED beside the mouse will turn white and the buzzer will make a short high-pitched beep. When exiting scroll mode, the mode LED will go back to its original colour, and the buzzer will make another short high-pitched beep of a different tone.

## Gamepad Mode Controls

The Forest Hub is able to simulate an HID Gamepad, including joystick movement and gamepad buttons 1-4. These buttons represent different actions depending on if it is being used directly on PC, on mobile, or being used on the XAC. To see the mapping of the inputs see the table above under “Device Controls.” When the switch is activated the button will be pressed, and when the switch is released the button will release.

## Forest Hub Settings Controls

### Slot and Mode Change Overview

Changing the slot and operating mode of the Forest Hub can be done using the Mode button on the Hub itself or using the SM switch.

A slot change is done using a short press (< 3 seconds), and a mode change is done using a long press (> 3 seconds). This is indicated on the enclosure using a dot and a dash, shown below.

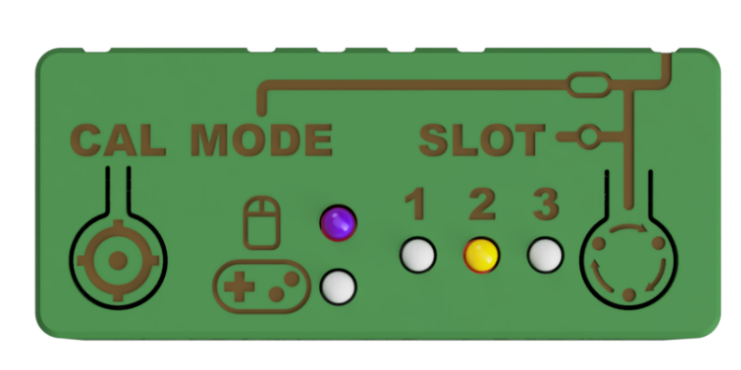
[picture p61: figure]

Mode Button

Short Press Icon

Long Press Icon

#### Cycle Slot

To change the slot, perform a short press (< 3 seconds) of either assistive switch SM or the Mode button on the Forest Hub. When the switch or button is released, the slot LED will change. The default is slot 0, which has no slot LEDs lit up. The slots will cycle from Slot 0 > Slot 1 > Slot 2 > Slot 3 > Slot 0 … repeating.

When in Mouse Mode, the slots will change the mouse cursor speed. When in Gamepad Mode, the slots currently do not have a function.

#### Change Mode

To change the mode, perform a long press (> 3 seconds) of either assistive switch SM or the Mode button on the Forest Hub until the mode LED changes. The Forest Hub will then change from the current mode to the other, either from Mouse Mode to Gamepad Mode or from Gamepad Mode to Mouse Mode. When the mode is changed, the device will reset and perform the startup sequence.

### Calibration - Center Reset

A Center Reset resets the neutral position of the joystick in its resting position. If the position of the cursor is moving when the joystick is released and stationary, a Center Reset can help resolve the cursor drift.

A center reset is automatically performed when the Forest Hub is first powered on, or can be started manually:

1. Release the joystick to neutral.
2. Perform a short press (< 3 seconds) of the calibration button on the Forest Hub.

After initiating a Center Reset, both Mode LEDs will light up white momentarily, and then return to indicating the current mode in the original colour. Do not touch the joystick while both Mode LEDs are white.

# Specifications

Enclosure Height | 32 mm
Enclosure Depth | 46 mm
Enclosure Length | 108 mm

# Cleaning

The outside of the enclosure can be cleaned with a damp cloth. Do not use hot water. Do not submerge.

# Troubleshooting

Mouse cursor or gamepad joystick is drifting

- Ensure there is an analog joystick plugged into the J port
- Initiate a center reset by either:
  - Performing a short press of the calibration button
  - Disconnecting and reconnecting power

Mouse cursor is not visible

- Make sure device is connected
- Make sure device is in proper operating mode (e.g., Mouse not Gamepad)
- Make sure the device has proper onscreen settings (e.g., AssistiveTouch on iOS)

Mouse cursor is difficult to see

- Adjust the size or color of the cursor on the host device

Cursor movement is too slow or too fast

- Change the slot on the Forest to adjust cursor speed
- Adjust the cursor speed on the host device

Difficulty inputting a double-click

- Adjust the double click rate setting on the host device(s).

© 2023-2024 by Neil Squire Society. This work is licensed under the CC BY SA 4.0 License: http://creativecommons.org/licenses/by-sa/4.0 Files available at https://github.com/makersmakingchange/Forest-Joystick-Mouse-Hub Page 1 of 24

V2.1 | APRIL 2024 Forest Hub user Guide

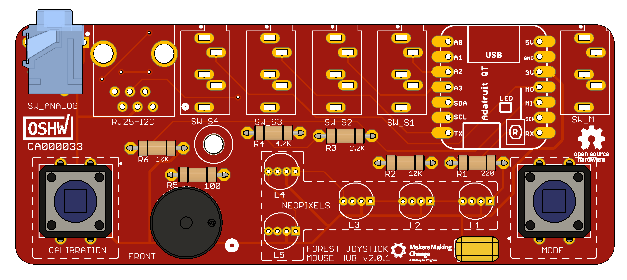
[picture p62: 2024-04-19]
Documentation/Working_Documents/Assets/PCB_Assembly/A11_Analog.png

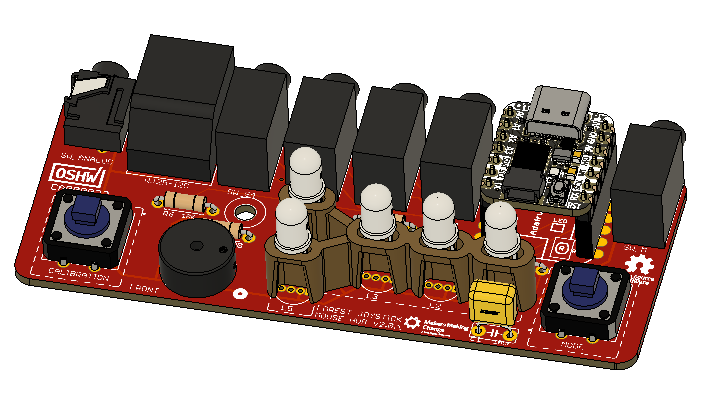
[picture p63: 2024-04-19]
Documentation/Working_Documents/Assets/PCB_Assembly/A23_Complete_PCB.png

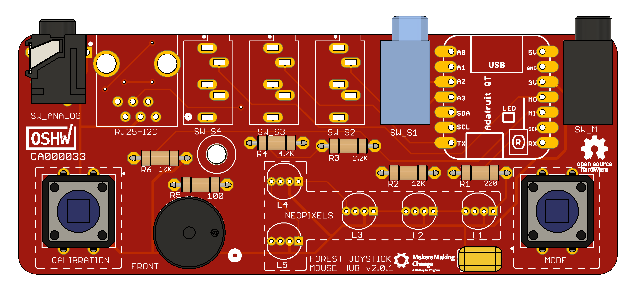
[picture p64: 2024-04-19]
Documentation/Working_Documents/Assets/PCB_Assembly/A13_SW_S1.png

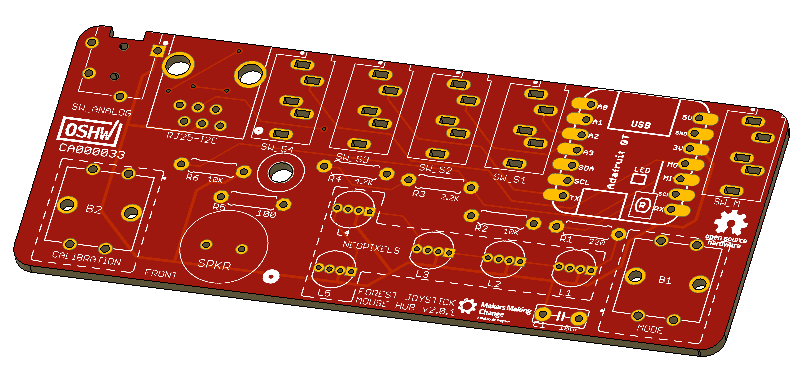
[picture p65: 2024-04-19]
Documentation/Working_Documents/Assets/PCB_Assembly/A00_PCB.png

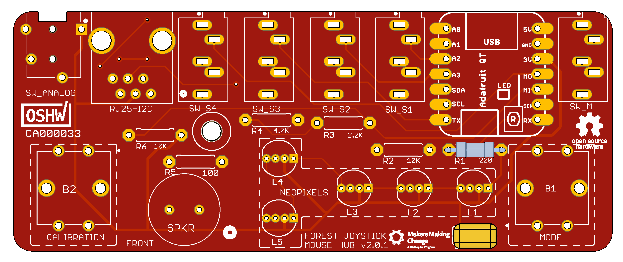
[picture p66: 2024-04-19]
Documentation/Working_Documents/Assets/PCB_Assembly/A02_R1.png

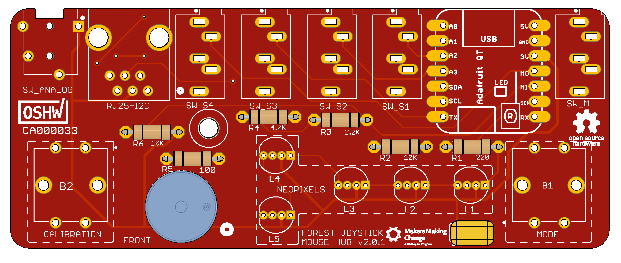
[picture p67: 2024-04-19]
Documentation/Working_Documents/Assets/PCB_Assembly/A08_SPKR.png

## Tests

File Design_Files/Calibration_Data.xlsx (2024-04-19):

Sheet: Sheet1
ID | rawX | rawY | JOYSTICK_INPUT_XY_MAX | JOYSTICK_MAX_VALUE | inputX | inputY | xNeutral | yNeutral | centeredX | centeredY
 | 0 | 490 | 1023 | 127 | -127 | -5 | 3 | -7 | -130 | -8
 | 1 | 490 | 1023 | 127 | -126 | -5 | 3 | -7 | -129 | -8
 | 2 | 490 | 1023 | 127 | -126 | -5 | 3 | -7 | -129 | -8
 | 3 | 490 | 1023 | 127 | -126 | -5 | 3 | -7 | -129 | -8
 | 4 | 490 | 1023 | 127 | -126 | -5 | 3 | -7 | -129 | -8
 | 5 | 490 | 1023 | 127 | -125 | -5 | 3 | -7 | -128 | -8
 | 6 | 490 | 1023 | 127 | -125 | -5 | 3 | -7 | -128 | -8
 | 7 | 490 | 1023 | 127 | -125 | -5 | 3 | -7 | -128 | -8
 | 8 | 490 | 1023 | 127 | -125 | -5 | 3 | -7 | -128 | -8
 | 9 | 490 | 1023 | 127 | -124 | -5 | 3 | -7 | -127 | -8
 | 10 | 490 | 1023 | 127 | -124 | -5 | 3 | -7 | -127 | -8
 | 11 | 490 | 1023 | 127 | -124 | -5 | 3 | -7 | -127 | -8
 | 12 | 490 | 1023 | 127 | -124 | -5 | 3 | -7 | -127 | -8
 | 13 | 490 | 1023 | 127 | -123 | -5 | 3 | -7 | -126 | -8
 | 14 | 490 | 1023 | 127 | -123 | -5 | 3 | -7 | -126 | -8
 | 15 | 490 | 1023 | 127 | -123 | -5 | 3 | -7 | -126 | -8
 | 16 | 490 | 1023 | 127 | -123 | -5 | 3 | -7 | -126 | -8
 | 17 | 490 | 1023 | 127 | -122 | -5 | 3 | -7 | -125 | -8
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

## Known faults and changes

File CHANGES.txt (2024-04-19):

Version 2.1 | 2024-Apr-17
 - Firmware
  - Added neutral calibration
 - User Guide
     - Expanded, with more details
     - Includes features from firmware version 2.1
     - New input mapping table 
     - Includes connection diagrams
 - Maker Guide
  - Updated PCB images
  - Better description of LED installation
 - CAD
  - Modified LED Spacer for easier installation

Version 2.0.1 | 2024-Feb-21
 - BOM
   - Fixed labels for R2, R5, R6
   - Removed erroneous modular connector
   - Fixed unit cost calculation
 - PCB
   - Increased pin distance on capacitor footprint
   - Add value for R5
   - Cleaned up top silkscreen on PCB
   - Removed polarity markers from speaker footprint

Version 2.0 | 2024-Jan-15
 - Updated PCB
  - Modified wiring for I2C connection to match LipSync
  - Moved mounting hole
 - Updated enclosure
   - Larger knockout for USB port  

Version 1.01 | 2023-Oct-27
 - Updated PCB
   - Added OSHWA certification logo
   - Larger resistor footprint

Version 1.0 | 2023-Sep-28
 - Initial Version
    - 4 Assistive Switch Inputs Jacks
    - 1 Mode Switch Input Jack
    - 1 Analog TRRS Joystick Input Jack
    - 1 RJ25 I2C Jack
    - 1 Mode Switch Button
    - 1 Calibration Button
    - 5 Neopixel indicators; 3 for Slot, 2 for Mouse/Joystick Output
 - Custom PCB
 - Adafruit Qt Py SAMD21 Microcontroller Dev Board
 -

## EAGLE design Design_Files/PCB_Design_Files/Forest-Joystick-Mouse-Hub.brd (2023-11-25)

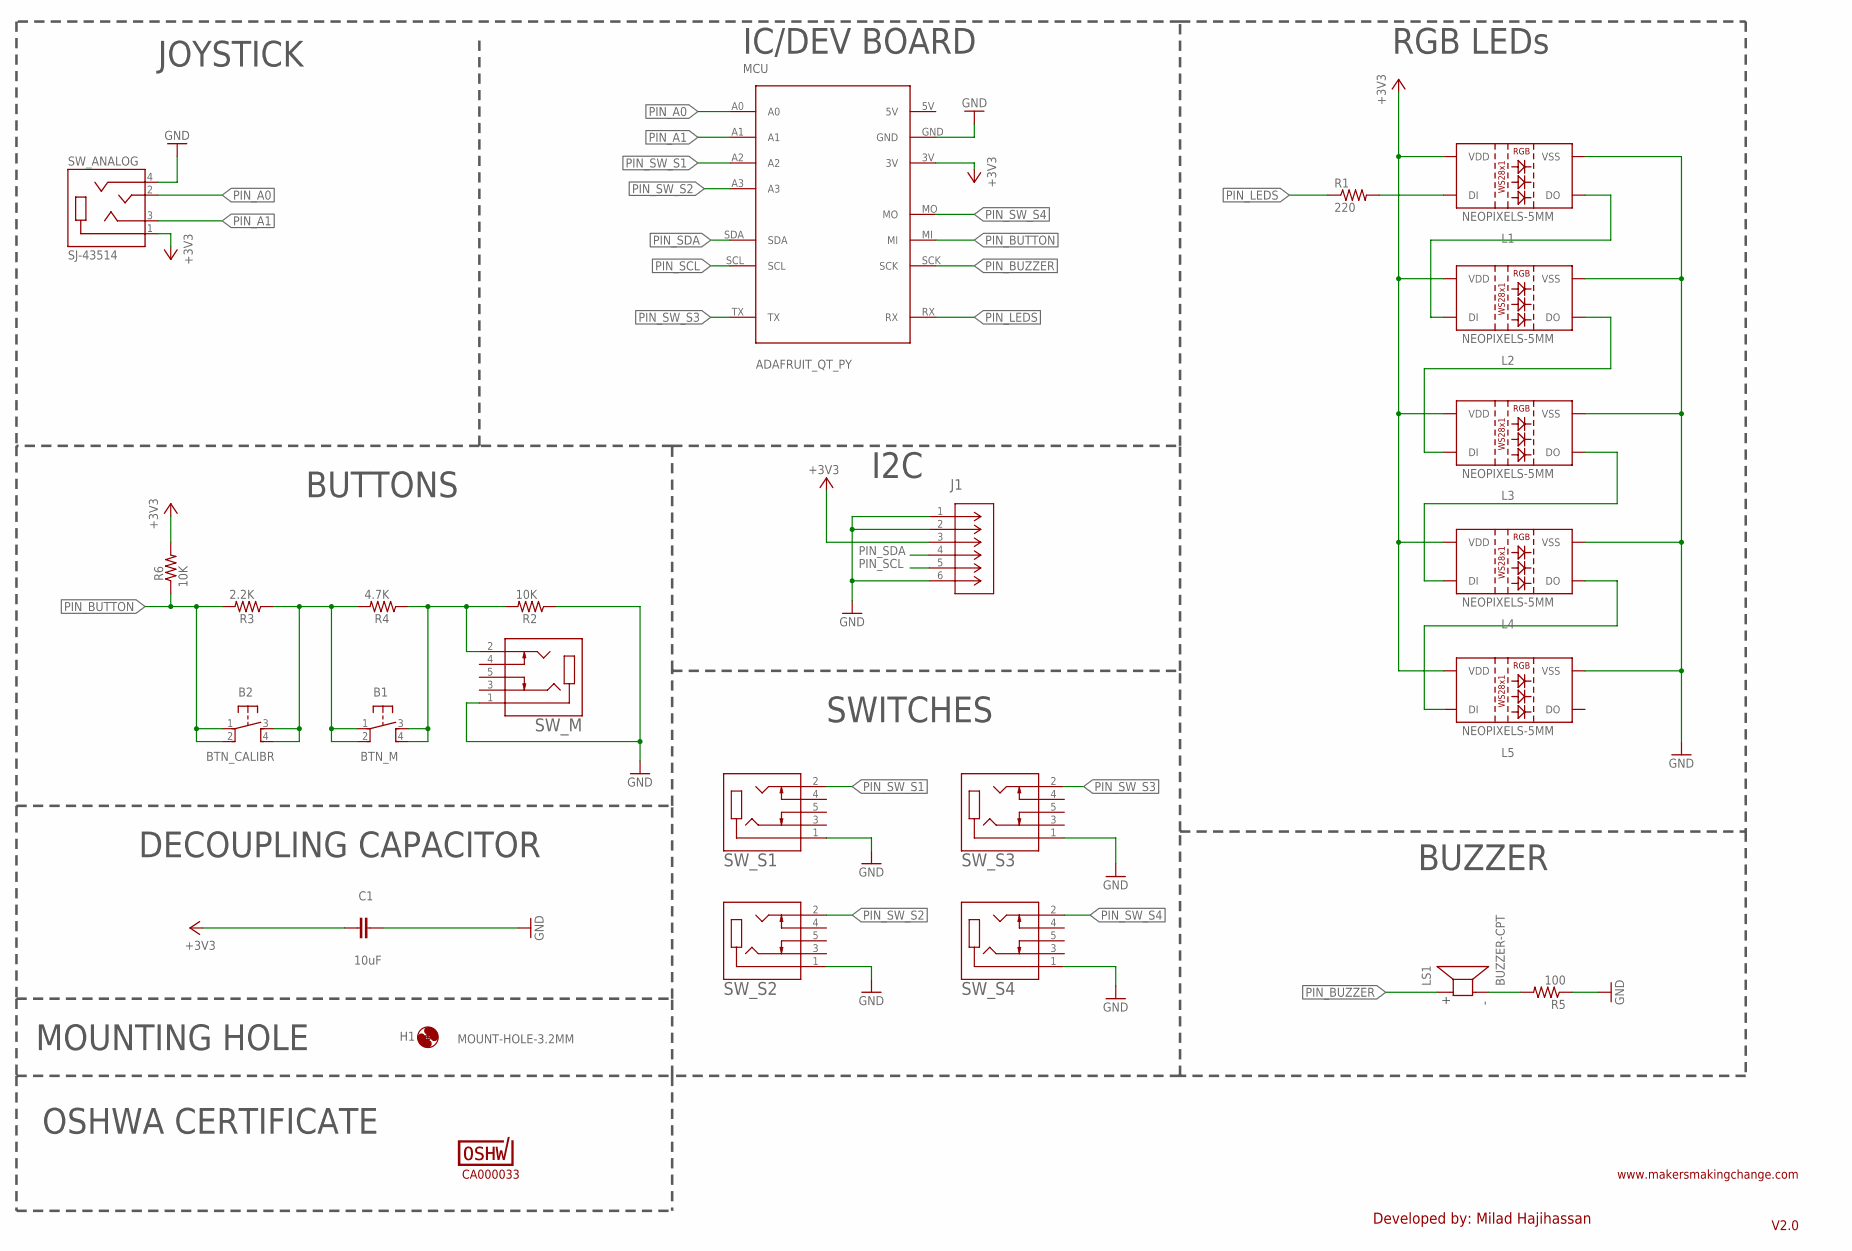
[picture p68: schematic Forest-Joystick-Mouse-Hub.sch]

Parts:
B1: BTN_M; B3F-5050
B2: BTN_CALIBR; B3F-5050
C1: 10uF; CAP-025-025X040
H1: MOUNT-HOLE-3.2MM; HOLE-3.2MM
J1: 5555165-1; CONN6_5555165-1
L1, L2, L3, L4, L5: NEOPIXELS-5MM
LOGO-OSHWA: CA000033; OSHWA-CERT-SMALL-SILK
LS1: BUZZER-CPT; CUI_CPT-1255C-090
MCU: ADAFRUIT_QT_PY; QT_PY
R1: 220; RESISTOR_0206/8
R2, R6: 10K; RESISTOR_0206/8
R3: 2.2K; RESISTOR_0206/8
R4: 4.7K; RESISTOR_0206/8
R5: 100; RESISTOR_0206/8
SW_ANALOG: SJ-43514; CUI_SJ-43514
SW_M: CUI_SJ1-3535NGSJ1-3535NG; CUI_SJ1-3535NG
SW_S1, SW_S2, SW_S3, SW_S4: CUI_SJ1-3535NGSJ1-3535NG; CUI_SJ1-3535NG

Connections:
+3V3: C1.1, J1.3, L1.P2 (VDD), L2.P2 (VDD), L3.P2 (VDD), L4.P2 (VDD), L5.P2 (VDD), MCU.3V, R6.2, SW_ANALOG.1 (SLEEVE)
GND: C1.2, J1.1, J1.2, J1.6, L1.P3 (VSS), L2.P3 (VSS), L3.P3 (VSS), L4.P3 (VSS), L5.P3 (VSS), MCU.GND, R2.1, R5.1, SW_ANALOG.4 (RING2), SW_M.1, SW_S1.1, SW_S2.1, SW_S3.1, SW_S4.1
unnamed: B1.1, B1.2, B2.3, B2.4, R3.1, R4.2
unnamed: L1.P4 (DO), L2.P1 (DI)
unnamed: B1.3, B1.4, R2.2, R4.1, SW_M.2
unnamed: L2.P4 (DO), L3.P1 (DI)
unnamed: L3.P4 (DO), L4.P1 (DI)
unnamed: L4.P4 (DO), L5.P1 (DI)
unnamed: L1.P1 (DI), R1.2
unnamed: LS1.N, R5.2
PIN_A0: MCU.A0, SW_ANALOG.2 (TIP)
PIN_A1: MCU.A1, SW_ANALOG.3 (RING1)
PIN_BUTTON: B2.1, B2.2, MCU.MI, R3.2, R6.1
PIN_BUZZER: LS1.P, MCU.SCK
PIN_LEDS: MCU.RX, R1.1
PIN_SCL: J1.5, MCU.SCL
PIN_SDA: J1.4, MCU.SDA
PIN_SW_S1: MCU.A2, SW_S1.2
PIN_SW_S2: MCU.A3, SW_S2.2
PIN_SW_S3: MCU.TX, SW_S3.2
PIN_SW_S4: MCU.MO, SW_S4.2

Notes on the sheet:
V2.0
Developed by: Milad Hajihassan
www.makersmakingchange.com
BUZZER
RGB LEDs
BUTTONS
I2C
IC/DEV BOARD
SWITCHES
JOYSTICK
MOUNTING HOLE
DECOUPLING CAPACITOR
OSHWA CERTIFICATE

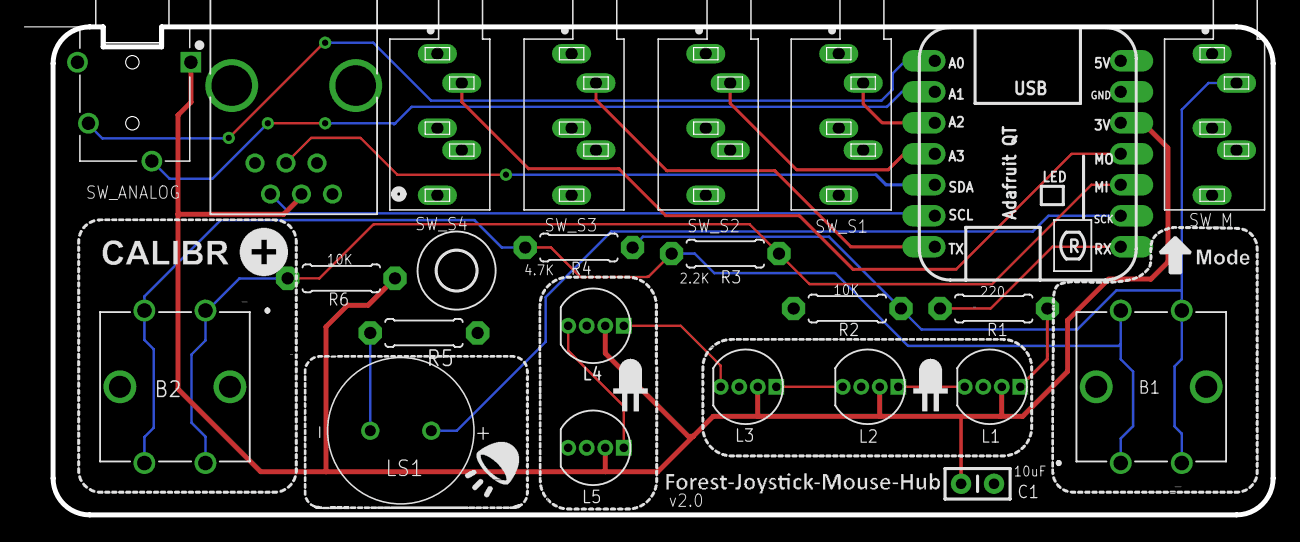
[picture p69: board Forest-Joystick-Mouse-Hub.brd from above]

Board: 2 copper layers, 102.3 x 40.0 mm, 25 parts (1 on the bottom side), 21 nets.

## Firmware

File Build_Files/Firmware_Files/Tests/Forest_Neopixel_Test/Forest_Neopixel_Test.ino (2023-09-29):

#include <Adafruit_NeoPixel.h> //Lights on QtPy

// ==================== Pin Assignment =================

#define PIN_JOYSTICK_X    A0
#define PIN_JOYSTICK_Y    A1
#define PIN_SW_S1         A2
#define PIN_SW_S2         A3
#define PIN_SW_S3         A6 //TX
#define PIN_SW_S4         A10 //MO
#define PIN_BUTTON        A9 //MI
#define PIN_LEDS          A7 //RX
#define PIN_BUZZER        A8 //SCK

Adafruit_NeoPixel leds(5, PIN_LEDS,NEO_GRB + NEO_KHZ800);  // Create a pixel strand with 5 pixels on QtPy
int ledsBrightness = 50;

void setup() {
  leds.begin();
  leds.setBrightness(ledsBrightness);
  leds.setPixelColor(0,leds.Color(0,255,0)); //red g r b
  leds.setPixelColor(1,leds.Color(165,255,0)); //orange
  leds.setPixelColor(2,leds.Color(255,255,0)); //yellow
  leds.setPixelColor(3,leds.Color(255,0,0)); //green
  leds.setPixelColor(4,leds.Color(0,0,255)); //blue
  leds.show();

}

void loop() {
  // put your main code here, to run repeatedly:

}

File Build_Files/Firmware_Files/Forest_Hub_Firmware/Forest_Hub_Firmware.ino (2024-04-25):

/*
  File: OpenAT_Joystick_Software.ino
  Software: OpenAT Joystick Plus 4 Switches, with both USB gamepad and mouse funtionality.
  Developed by: Makers Making Change
  Version: V2.1.rc1 (XX March 2024)
  License: GPL v3

  Copyright (C) 2023-2024 Neil Squire Society
  This program is free software: you can redistribute it and/or modify it under the terms of
  the GNU General Public License as published by the Free Software Foundation,
  either version 3 of the License, or (at your option) any later version.
  This program is distributed in the hope that it will be useful, but WITHOUT ANY WARRANTY;
  without even the implied warranty of MERCHANTABILITY or FITNESS FOR A PARTICULAR PURPOSE.
  See the GNU General Public License for more details.
  You should have received a copy of the GNU General Public License along with this program.
  If not, see <http://www.gnu.org/licenses/>
*/
#include <Arduino.h>
#include "XACGamepad.h"
#include "OpenAT_Joystick_Response.h"
#include <FlashStorage.h> // Non-volatile memory for storing settings
#include <TinyUSB_Mouse_and_Keyboard.h> // Library to allow mouse and keyboard to work using TinyUSB
#include <WiiChuck.h> // Nunchuck communication
#include <Adafruit_NeoPixel.h> // Lights on QtPy


#define USB_DEBUG  0 // Set this to 0 for best performance.


//Define model number and version number
#define JOYSTICK_DEVICE   1                
#define JOYSTICK_MODEL    1
#define JOYSTICK_VERSION  2


// ==================== Pin Assignment =================

#define PIN_JOYSTICK_X    A0
#define PIN_JOYSTICK_Y    A1
#define PIN_SW_S1         A2
#define PIN_SW_S2         A3
#define PIN_SW_S3         A6  // TX on PCB
#define PIN_SW_S4         A10 // MO on PCB
#define PIN_BUTTON        A9  // MI on PCB
#define PIN_LEDS          A7  // RX on PCB
#define PIN_BUZZER        A8  // SCK on PCB


// 5 Neopixels connected in series
#define LED_SLOT0         5  // Non-existent Neopixel for no light
#define LED_SLOT1         2  // Neopixel index for slot 1   // L3 on PCB
#define LED_SLOT2         1  // Neopixel index for slot 2   // L2 on PCB
#define LED_SLOT3         0  // Neopixel index for slot 3   // L1 on PCB
#define LED_GAMEPAD       4  // Neopixel index for gamepad  // L5 on PCB
#define LED_MOUSE         3  // Neopixel index for mouse    // L4 on PCB
#define LED_MICRO         0  // Index of Neopixel on QTPY microcontroller
#define LED_DEFAULT_BRIGHTNESS 50
#define CONF_LED_COLOR_R_DEFAULT     255 // Default LED red channel
#define CONF_LED_COLOR_G_DEFAULT     0  // Default LED green channel
#define CONF_LED_COLOR_B_DEFAULT     0  // Default LED blue channel
#define LED_NUM_PIXELS    5  // number of neopixels
#define CONF_LED_COLOR_MIN 0 // Minimum LED color value
#define CONF_LED_COLOR_MAX 255  // Maximum LED color value
#define CONF_LED_COLOR_DEFAULT 125 // default

#define MODE_MOUSE 1
#define MODE_GAMEPAD 0
#define DEFAULT_MODE MODE_MOUSE

#define CONF_OPERATING_MODE_MIN 0
#define CONF_OPERATING_MODE_MAX 1
#define CONF_OPERATING_MODE_DEFAULT DEFAULT_MODE

#define CONF_LED_BRIGHTNESS_MIN 0
#define CONF_LED_BRIGHTNESS_MAX 255
#define CONF_LED_BRIGHTNESS_DEFAULT 127

#define CONF_LED_MIN 0
#define CONF_LED_MAX 255



#define UPDATE_INTERVAL   20 // TBD Update interval for perfoming HID actions (in milliseconds)
#define DEFAULT_DEBOUNCING_TIME 5

#define LONG_PRESS_MILLIS  3000 // time, in milliseconds, for a mode change to occur

#define SLOT_DEFAULT_NUMBER                  0             // Default slot number
#define SLOT_MIN_NUMBER                      0             // Minimum slot number
#define SLOT_MAX_NUMBER                      3             // Maxium slot number

#define JOYSTICK_DEFAULT_DEADZONE_LEVEL      2              // Joystick deadzone
#define JOYSTICK_MIN_DEADZONE_LEVEL          1  
#define JOYSTICK_MAX_DEADZONE_LEVEL          10
#define JOYSTICK_MAX_DEADZONE_VALUE          64             // Out of 127
#define JOYSTICK_MAX_VALUE                   127            // Maximum value for joystick output

#define JOYSTICK_INPUT_XY_MAX                1023            // Maximum sensor reading of joystick digitized voltage
#define JOYSTICK_NEUTRAL_DEFAULT             511             // Expected digitized analog voltage of joystick x channel when centered (511)

#define MOUSE_DEFAULT_CURSOR_SPEED_LEVEL     5              // Default cursor speed level
#define MOUSE_MIN_CURSOR_SPEED_LEVEL         1              // Minimum cursor speed level
#define MOUSE_MAX_CURSOR_SPEED_LEVEL         10             // Maxium cursor speed level
#define MOUSE_MIN_CURSOR_SPEED_VALUE         4              // Minimum cursor speed value [pixels per update]
#define MOUSE_MAX_CURSOR_SPEED_VALUE         40

#define JOYSTICK_REACTION_TIME               30             // Minimum time between each action in ms
#define SWITCH_REACTION_TIME                 100            // Minimum time between each switch action in ms
#define STARTUP_DELAY_TIME                   1000           // Time to wait on startup
#define FLASH_DELAY_TIME                     5              // Time to wait after reading/writing flash memory

#define SLOW_SCROLL_DELAY                    200            // Minimum time, in ms, between each slow scroll action (number of slow scroll actions defined below)
#define FAST_SCROLL_DELAY                    60             // Minimum time, in ms, between each fast scroll action (higher delay = slower scroll speed)
#define SLOW_SCROLL_NUM                      10             // Number of times to scroll at the slow scroll rate

const int MODE_START_TONE = 880;
const int MODE_MOUSE_TONE = 523;
const int MODE_GAMEPAD_TONE = 1047;
const int MODE_START_TONE_LENGTH = 500;
const int MODE_MOUSE_TONE_LENGTH = 400;
const int MODE_GAMEPAD_TONE_LENGTH = 600;
const int SLOT_TONE = 1319;
const int SLOT_TONE_LENGTH = 200;
const int SLOT_TONE_DELAY = 300;
const int SCROLL_START_TONE = 2093;
const int SCROLL_END_TONE = 2637;
const int SCROLL_TONE_LENGTH = 200;

XACGamepad gamepad;   //Starts an instance of the USB gamepad object

//Declare variables for settings
bool isConfigured;
int deviceNumber;
int modelNumber;
int versionNumber;
int deadzoneLevel;
int cursorSpeedLevel; // 1-10 cursor speed levels
int operatingMode;   // 1 = Mouse mode, 0 = Joystick Mode 
int slotNumber;      // Slots numbered 1-3 with different settings
int ledColorR = CONF_LED_COLOR_R_DEFAULT;  // User color - red
int ledColorG = CONF_LED_COLOR_G_DEFAULT;  // User color - green
int ledColorB = CONF_LED_COLOR_B_DEFAULT;  // User color - blue 
int ledBrightness;  // Neopixel LED brightness

// Variables stored in Flash Memory
FlashStorage(isConfiguredFlash, bool);
FlashStorage(deviceNumberFlash,int);
FlashStorage(modelNumberFlash, int);
FlashStorage(versionNumberFlash, int);
FlashStorage(deadzoneLevelFlash, int);
FlashStorage(cursorSpeedLevelFlash, int);
FlashStorage(operatingModeFlash, int);
FlashStorage(ledBrightnessFlash,int);
FlashStorage(slotNumberFlash,int);  // Track index of current settings slot
FlashStorage(xOutputMinimumFlash,int);  // Calibration
FlashStorage(xOutputMaximumFlash,int);  // Calibration
FlashStorage(yOutputMinimumFlash,int);  // Calibration
FlashStorage(yOutputMaximumFlash,int);  // Calibration
FlashStorage(xNeutralFlash,int);  // Calibration
FlashStorage(yNeutralFlash,int);  // Calibration

FlashStorage(ledColorRFlash,int);  // User LED color - red
FlashStorage(ledColorGFlash,int);  // User LED color - green
FlashStorage(ledColorBFlash,int);  // User LED color - blue

// Timing Variables
long lastInteractionUpdate;
long mPressStartMillis = 0;
long cPressStartMillis = 0;

//Declare joystick input and output variables
int rawX = JOYSTICK_INPUT_XY_MAX/2; // Raw digitized analog voltage of joystick x channel (511)
int rawY = JOYSTICK_INPUT_XY_MAX/2; // Raw digitized analog voltage of joystick y channel (511)
int inputX;
int inputY;
int centeredX;
int centeredY;
int outputX;
int outputY;

//Declare joystick calibration variables
int xOutputMinimum = 0;  // Minimum digitized analog voltage of joystick x channel
int yOutputMinimum = 0;  // Minimum digitized analog voltage of joystick y channel
int xOutputMaximum = JOYSTICK_INPUT_XY_MAX;  // Maximum digitized analog voltage of joystick x channel (1023)
int yOutputMaximum = JOYSTICK_INPUT_XY_MAX;  // Maximum digitized analog voltage of joystick y channel (1023)
int xNeutral = JOYSTICK_NEUTRAL_DEFAULT; //  Expected digitized analog voltage of joystick x channel when centered (511)
int yNeutral = JOYSTICK_NEUTRAL_DEFAULT; //  Expected digitized analog voltage of joystick y channel when centered (511)

float minRange;    // TODO: change this name

bool isModeChanging;

//Declare switch state variables for each switch
bool switchS1Pressed = false;           // Mouse mode = left click
bool switchS2Pressed= false;            // Mouse mode = scroll mode
bool switchS3Pressed= false;            // Mouse mode = right click
bool switchS4Pressed= false;            // Mouse mode = middle click
bool switchSMPressed= false; 
bool buttonCPressed= false; 
bool buttonMPressed= false; 

//Previous status of switches
bool switchS1PrevPressed = false;
bool switchS2PrevPressed = false;
bool switchS3PrevPressed = false;
bool switchS4PrevPressed = false;
bool switchSMPrevPressed = false;
bool buttonCPrevPressed  = false;
bool buttonMPrevPressed  = false;

bool scrollModeOn = false;

// Theoretical voltages for multi-button analog resistor network
// SM_Switch - Mode Switch - Calib Switch
// voltages v000 = voltage when off-off-off
const int v000 = 643;
const int v001 = 609;
const int v010 = 563;
const int v011 = 512;
const int v100 = 418;
const int v101 = 327;
const int v110 = 185;
const int v111 = 0;
// thresholds
const int t001 = (v000+v001)/2;
const int t010 = (v001+v010)/2;
const int t011 = (v010+v011)/2;
const int t100 = (v011+v100)/2;
const int t101 = (v100+v101)/2;
const int t110 = (v101+v110)/2;
const int t111 = (v110+v111)/2;

int currentDeadzoneValue;
int currentMouseCursorSpeedValue;

bool settingsEnabled = false;

//***API FUNCTIONS***// - DO NOT CHANGE
typedef void (*FunctionPointer)(bool, bool, String);

//Type definition for API function pointer

typedef struct {                                  //Type definition for API function list
  String endpoint;                                //Unique two character end point
  String code;                                    //Unique one character command code
  String parameter;                               //Parameter that is passed to function
  FunctionPointer function;                       //API function pointer
} _functionList;

//Switch structure
typedef struct {
  uint8_t switchNumber;
  String switchButtonName;
  uint8_t switchButtonNumber;
} switchStruct;

// Slot structure
typedef struct {
  uint8_t slotNumber;
  uint8_t slotLEDNumber;
  String mouseSlotName;
  int slotCursorSpeedLevel;
} slotStruct; 
/*
 * To add to Slot Structure later:
 * - mouse acceleration
 * - mouse switch functions (so these can be remapped)
 * - gamepad slot name
 * - gamepad switch functions
 * - deadzone??
 */
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

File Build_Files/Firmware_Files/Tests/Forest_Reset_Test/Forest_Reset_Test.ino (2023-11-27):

#include "Reset.h"
#include <Adafruit_NeoPixel.h> //Lights on QtPy

// ==================== Pin Assignment =================

const int PIN_JOYSTICK_X =  A0;
const int PIN_JOYSTICK_Y =  A1;
const int PIN_SW_S1 =       A2;
const int PIN_SW_S2 =       A3;
const int PIN_SW_S3 =       A6; //TX
const int PIN_SW_S4 =       A10; //MO
const int PIN_BUTTON =      A9; //MI
const int PIN_LEDS =        A7; //RX
const int  PIN_BUZZER =     A8; //SCK

Adafruit_NeoPixel leds(5, PIN_LEDS,NEO_GRB + NEO_KHZ800);  // Create a pixel strand with 5 pixels on QtPy
int ledsBrightness = 50;

bool switchS1State;
bool switchS2State;
bool switchS3State;
bool switchS4State;
int buttonState;
bool switchSMState;
bool buttonCState;
bool buttonMState;

bool switchS1PrevState = false;
bool switchS2PrevState = false;
bool switchS3PrevState = false;
bool switchS4PrevState = false;
bool switchSMPrevState = false;
bool buttonCPrevState = false;
bool buttonMPrevState = false;

const int thresholdCount = 7;
const int t001 = (644+610)/2;
const int t010 = (610+563)/2;
const int t011 = (563+513)/2;
const int t100 = (513+419)/2;
const int t101 = (419+327)/2;
const int t110 = (327+185)/2;
const int t111 = (185+1)/2;
const int thresholds[thresholdCount]={t111,t110,t101,t100,t011,t010,t001};


unsigned long buttonPressStartTime = 0;
const unsigned long requiredPressDuration = 2000;


void setup() {
  
// Begin serial
  Serial.begin(115200);
  
  leds.begin();
  leds.setBrightness(ledsBrightness);
  leds.clear();
  leds.show();

    //Initialize the switch pins as inputs
  pinMode(PIN_SW_S1,  INPUT_PULLUP);
  pinMode(PIN_SW_S2,  INPUT_PULLUP);
  pinMode(PIN_SW_S3,  INPUT_PULLUP);
  pinMode(PIN_SW_S4,  INPUT_PULLUP);
  pinMode(PIN_BUTTON, INPUT);  

}

void loop() {
 
  switchS1State = !digitalRead(PIN_SW_S1);
  switchS2State = !digitalRead(PIN_SW_S2);
  switchS3State = !digitalRead(PIN_SW_S3);
  switchS4State = !digitalRead(PIN_SW_S4);

  buttonState = analogRead(PIN_BUTTON);

 if (buttonState < t111)
 {
  switchSMState = true;
  buttonMState = true;
  buttonCState = true;
 }
 else if (buttonState < t110)
 {
  switchSMState = true;
  buttonMState = true;
  buttonCState = false;
 }
 else if (buttonState < t101)
  {
  switchSMState = true;
  buttonMState = false;
  buttonCState = true;
 }
 else if (buttonState < t100)
  {
  switchSMState = true;
  buttonMState = false;
  buttonCState = false;
 }
  else if (buttonState < t011)
  {
  switchSMState = false;
  buttonMState = true;
  buttonCState = true;
 }
  else if (buttonState < t010)
  {
  switchSMState = false;
  buttonMState = true;
  buttonCState = false;
 }
  else if (buttonState < t001)
  {
  switchSMState = false;
  buttonMState = false;
  buttonCState = true;
 }
  else 
  {
  switchSMState = false;
  buttonMState = false;
  buttonCState = false;
 }
 
  
if (buttonMState == true && buttonMPrevState == false){
  buttonPressStartTime = millis();
}
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

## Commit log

2023-09-29 v1.0 Update
    [Forest-Joystick-Mouse-Hub.brd, Forest-Joystick-Mouse-Hub.sch, Forest_Hub_BOM.csv, Forest_Hub_BOM.xlsx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]
2023-09-30 PCB Files cleanup
    [Forest-Joystick-Mouse-Hub.brd, Forest-Joystick-Mouse-Hub.sch]
2023-10-01 Update resistor size
    [Forest-Joystick-Mouse-Hub.brd]
2023-10-01 Update Forest_Hub_Firmware.ino
    Add device number to API
2023-10-01 Update Forest_Button_Test.ino
    Working multi-button via analog pin
2023-10-01 Add LED Brightness parameter
2023-10-13 Update BOM
    Use two 7p headers rather than cheaper one you need to cut.
    [Forest_Hub_BOM.csv, Forest_Hub_BOM.xlsx]
2023-10-25 Update Forest_Hub_Firmware.ino
    Added variable for slot index in Flash memory
2023-10-25 Added slot structure
2023-10-28 PCB Updates
    - Footprint for larger resistors
    - Added OSHWA Certification logo
    - Updated Gerbers
    [Forest-Joystick-Mouse-Hub.brd, Forest-Joystick-Mouse-Hub.sch]
2023-10-28 Clean-up PCB build files
2023-10-31 Added saving slot to memory and loading slot on startup
2023-10-31 Changed logic for buttons and added slot functionality
2023-11-03 Changed LED colour and default slot
2023-11-03 Create Resistor_Network.xlsx
    Add spreadsheet for calculating nominal tolerances for analog resistor network.
    [Resistor_Network.xlsx]
2023-11-03 Update Forest_Hub_Design_Rationale.docx
    Add details on resistor network
2023-11-03 Update Forest_Hub_Firmware.ino
    Update resistor network values.
2023-11-25 PCB and Enclosure Update
    - Swapped RJ11 connector to match Sparkfun Breakout board / reduce number of parts
    - Swapped RJ11 wiring to match QWIIC adapter board / LipSync
    - Modified USB Knockout on Case
    -
    [Forest-Joystick-Mouse-Hub.brd, Forest-Joystick-Mouse-Hub.sch, Forest_Hub_BOM.csv, Forest_Hub_BOM.xlsx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]
2023-11-27 Update Forest_Hub_Firmware.ino
    rename slotChange to incrementSlot
2023-11-27 Basic slot implementation
    - added slot zero
    - added API for slot number change
2023-11-27 Update Forest_Hub_Firmware.ino
    default slot to 0
2023-11-27 Update Forest_Hub_Firmware.ino
    rename mouse slots
    fix cursor speed update with slot update
2023-11-27 Update Forest_Hub_Firmware.ino
    write slot to memory so it is persistent
2023-12-07 Savepoint 2023-Dec-7
    [Forest_Hub_BOM.xlsx]
2024-02-20 Update Forest_Hub_Firmware.ino
    Fix calibration variables.
2024-02-20 Updated documentation
    [Forest_Hub_BOM.xlsx]
2024-03-13 Basic neutral calibration working on startup
2024-03-14 Basic neutral calibration working through API and button press
2024-03-18 Functional neutral calibration that allows for output of full extents
2024-03-18 Remove old PCB design files
    [Forest-Joystick-Mouse-Hub_v0.1.brd, Forest-Joystick-Mouse-Hub_v0.1.sch]
2024-03-18 Update Forest_Hub_Firmware.ino
    Add Arduino.h library for future PlatformIO expansion
2024-04-12 Add updated PCB images
    PCB V2.0.1
2024-04-12 Add additional PCB screenshots
2024-04-18 Replace default LED Spacer
    [Forest_LED_Spacer-5Windows.stl, Forest_LED_Spacer.stl]
2024-04-18 Remove outdated PCB schematic and board pdfs
2024-04-23 Fixed bug
    Wasn't showing slot LED after neutral calibration
2024-04-29 Add PCB instructions to Maker Guide

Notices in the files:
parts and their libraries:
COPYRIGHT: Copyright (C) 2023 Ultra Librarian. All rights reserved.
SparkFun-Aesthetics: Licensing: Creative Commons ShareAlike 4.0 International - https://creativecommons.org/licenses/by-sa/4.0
